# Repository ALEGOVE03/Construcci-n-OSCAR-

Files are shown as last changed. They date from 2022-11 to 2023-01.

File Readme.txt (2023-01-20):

Este repositorio contiene todo lo necesario para construir OSCAR según las especificaciones del LIANA, se incluyen los archivos necesarios de manufactura de las piezas. Las cuales se desarrollaron mediante impresión 3D con filamento PLAmax, además se incluyen los archivos del PCB el cual se mandó a hacer en China. Para finalizar se incluyen los archivos de programación desarrollada mediante ROS noetic usando Python.

 El proyecto consiste en una plataforma robótica para hacer experimentos, cuenta con dos manipuladores THOR que se adaptaron según las necesidades del laboratorio y al ser modular cuenta con una gran flexibilidad para mejoras o cambios. Como parte de la documentación que se incluye están los planos, plan de manufactura, instrucciones de ensamble con lista de materiales y los archivos de programación documentado.

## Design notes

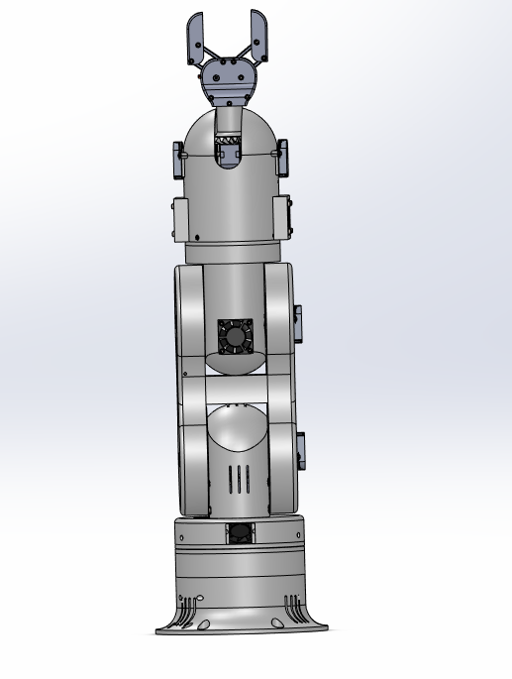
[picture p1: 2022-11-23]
OSCAR-THOR/STL/Sin título.png

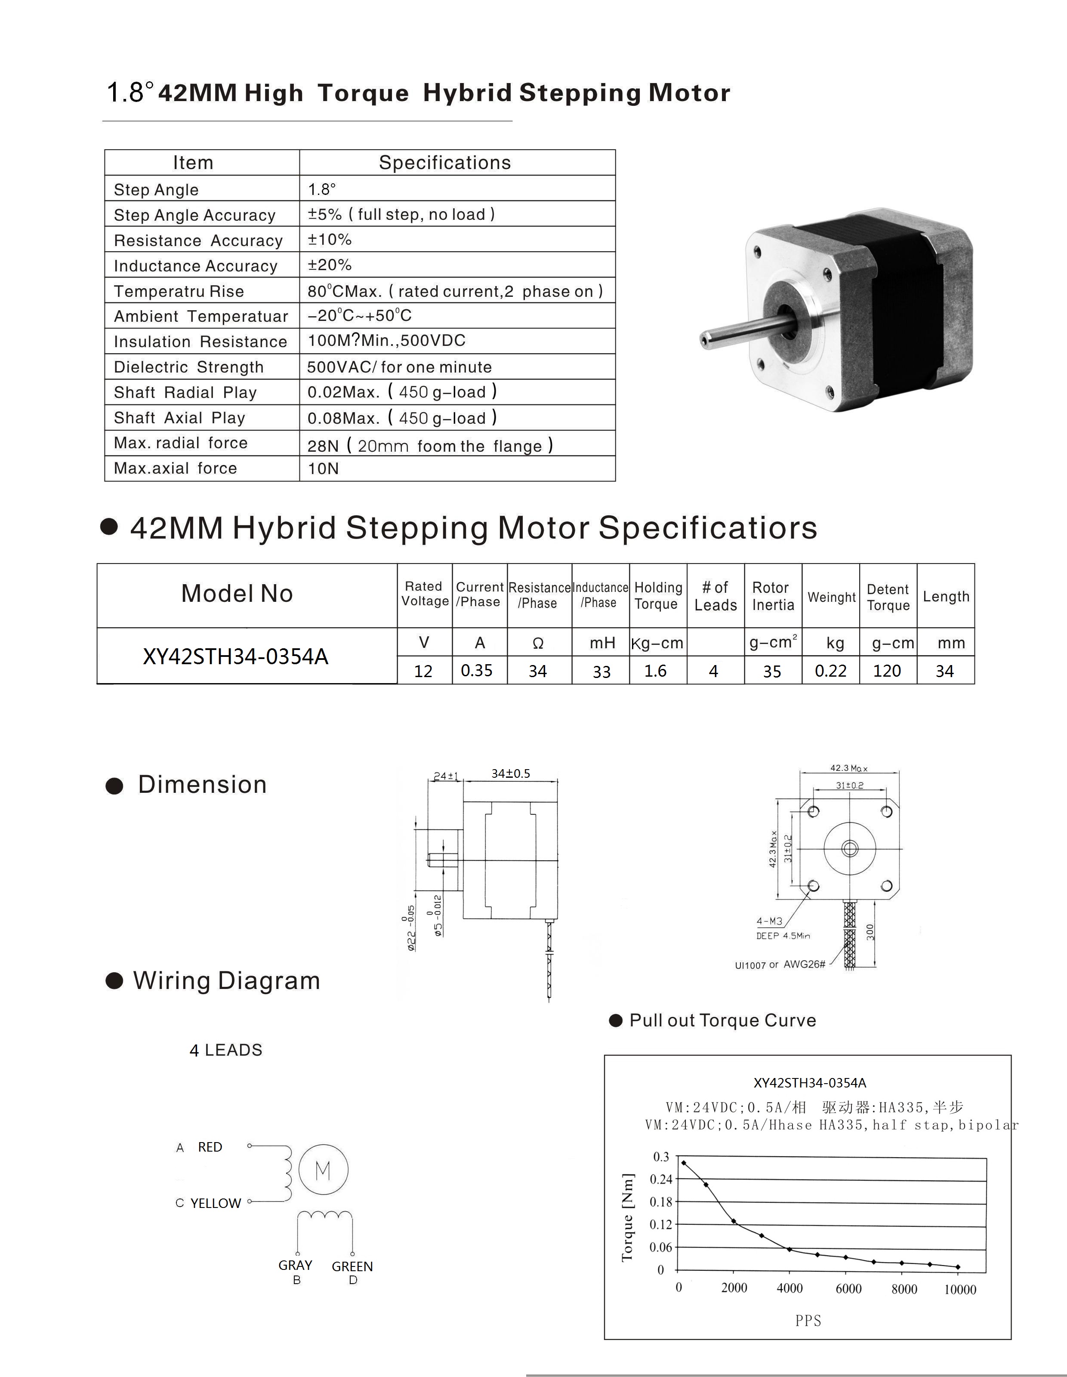
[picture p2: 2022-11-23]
Documentos/Hojas de datos/nema17_34_datasheet.jpg

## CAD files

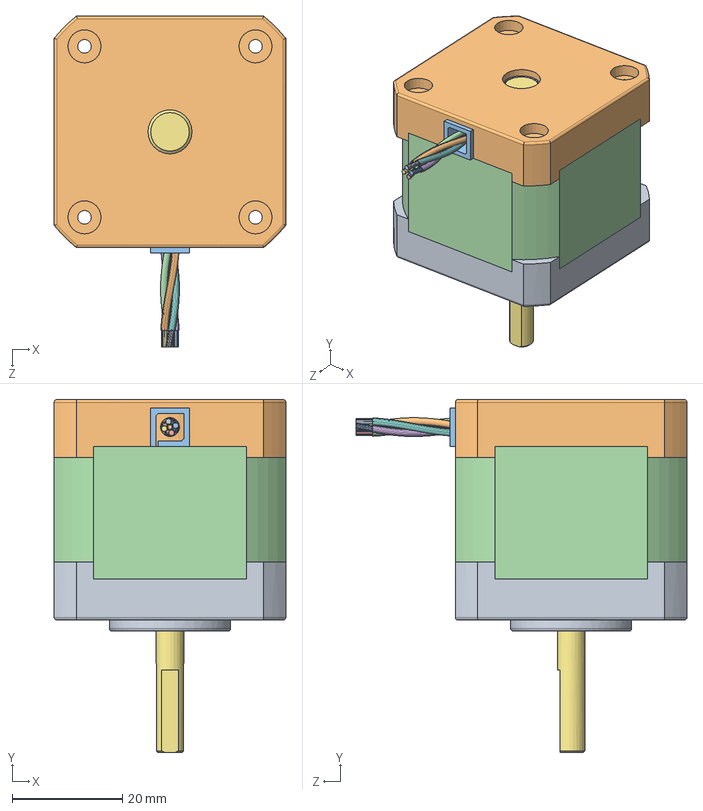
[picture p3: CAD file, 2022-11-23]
OSCAR-THOR/Componentes/NEMA17 x 40.SLDASM
42.0 x 64.0 x 60.0 mm
Frontplate.step
Backplate.step
Connenctor.step
Housing.step
Bearing dummy.step
Bearing dummy 01.step
Core.step
Cable-1of4.step
Copper-1of4.step
Cable-2of4.step
Copper-4of4.step
Cable-3of4.step
Copper-3of4.step
Cable-4of4.step
Copper-2of4.step

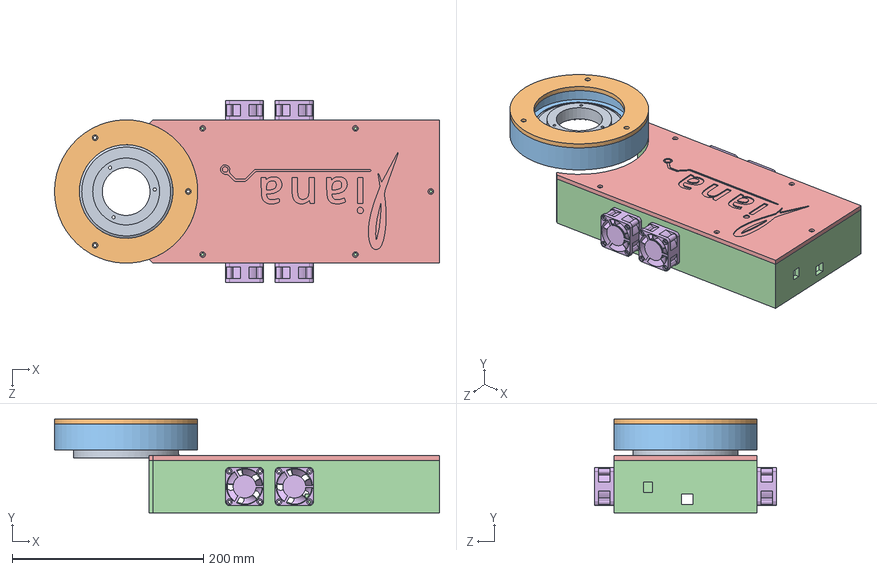
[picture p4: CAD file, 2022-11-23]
OSCAR-THOR/Ensamble URDF/Base_link/Base.SLDASM
402.9 x 98.0 x 190.0 mm
Art1Bot
BaseBearingFix
BaseTop
BaseCase
CaseTop}
40mm fan x 4

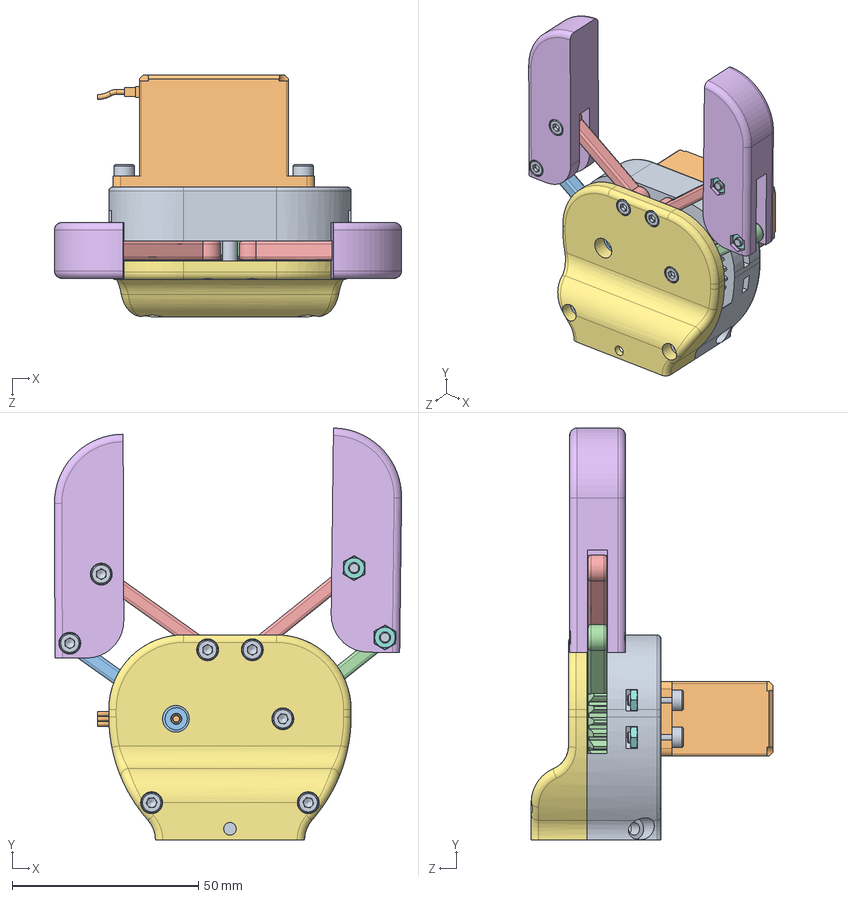
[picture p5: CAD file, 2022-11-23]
OSCAR-THOR/Ensamble URDF/Gripper/gripper.SLDASM
93.1 x 110.5 x 64.8 mm
GripperBot
MG996R
GripperActiveArm
GripperPassiveArm
GripperArm x 2
GripperFinger x 2
GripperTop
hexagon nut_3_jis x 13
socket head cap screw_am x 13

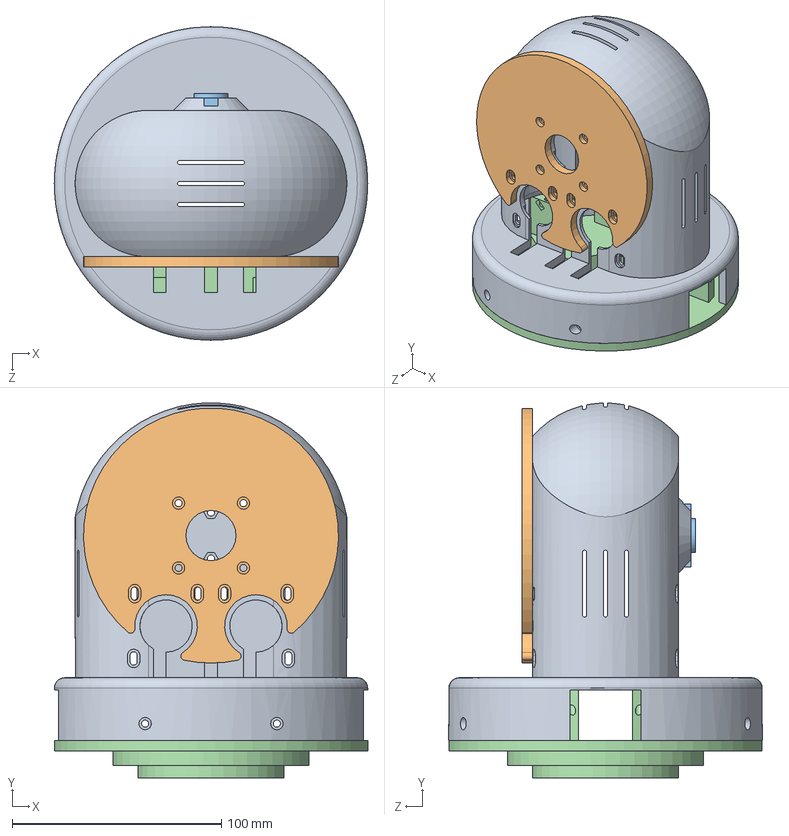
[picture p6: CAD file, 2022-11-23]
OSCAR-THOR/Ensamble URDF/Link_1/ART1.SLDASM
150.0 x 179.4 x 150.0 mm
Art1Body
Art2BodyACover1
AxisFix
Art1Top

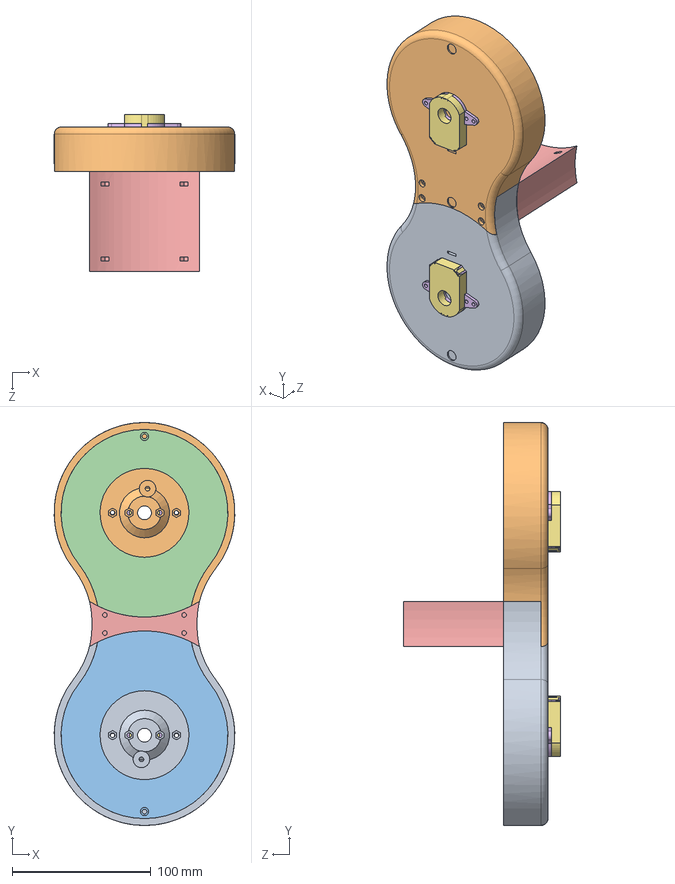
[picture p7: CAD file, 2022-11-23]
OSCAR-THOR/Ensamble URDF/Link_2/ART2_2.SLDASM
129.9 x 290.0 x 113.0 mm
Art2BodyB_Splitted_A
Art2BodyB_Splitted_B
Art2BodyBCover_Splitted_A
Art2BodyBCover_Splitted_B
Art2BodyUnion
AMT-B0-W x 2
AMT x 2

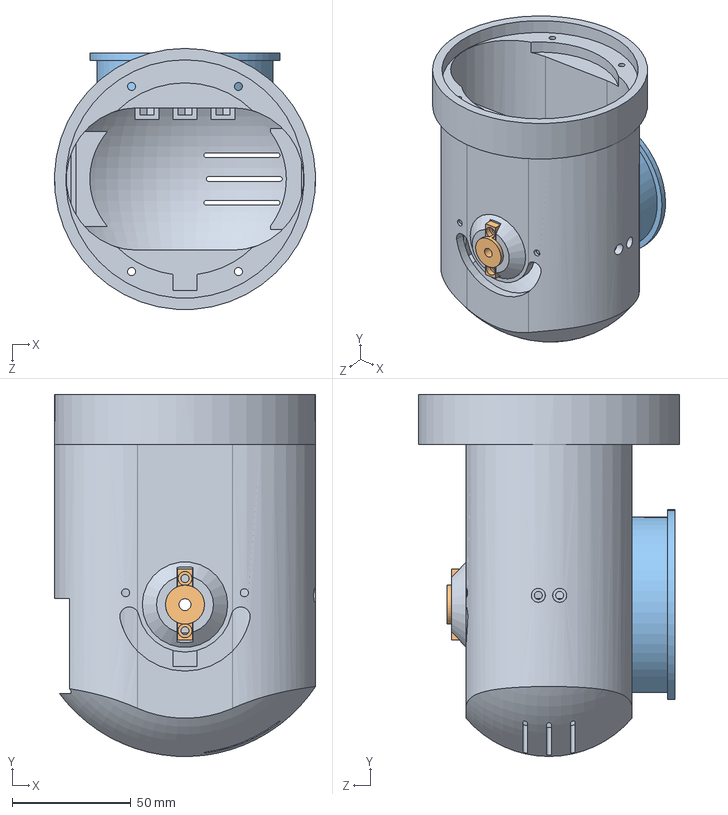
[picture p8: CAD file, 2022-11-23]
OSCAR-THOR/Ensamble URDF/Link_3/ART3&4.SLDASM
110.0 x 152.5 x 110.0 mm
Art3Body
AxisFix
Art3Pulley
CommonBearingFixThrough

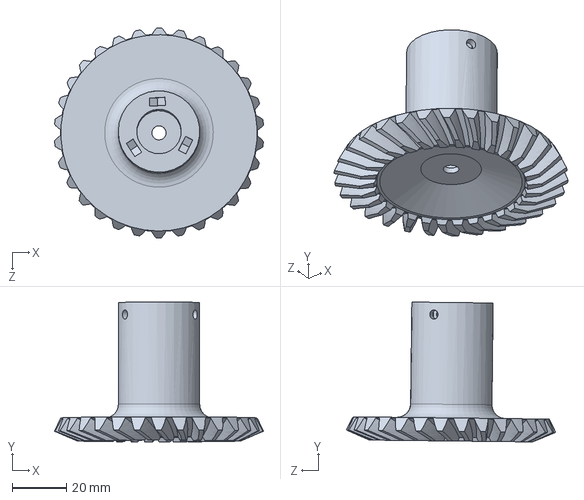
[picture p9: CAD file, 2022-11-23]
OSCAR-THOR/Ensamble URDF/Link_6/Link6.SLDASM
77.0 x 51.5 x 77.2 mm

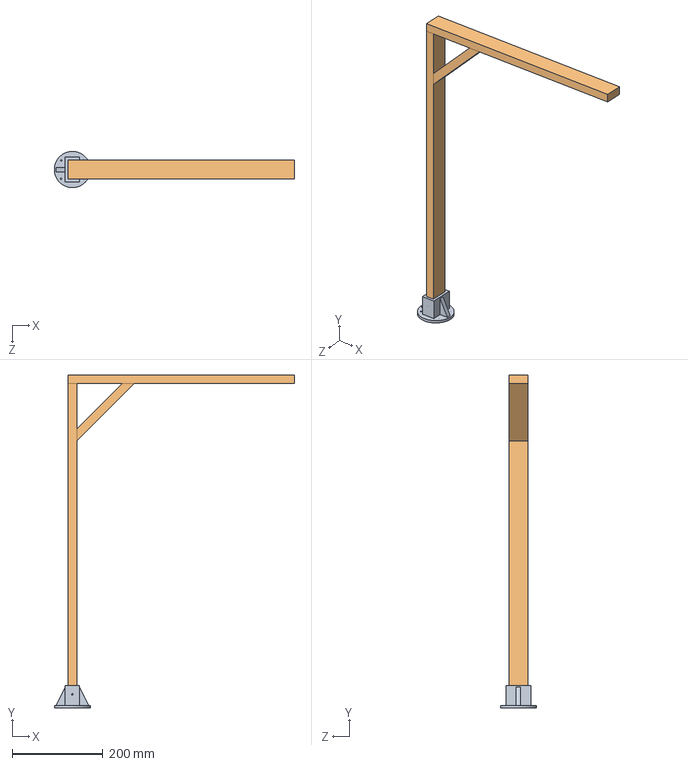
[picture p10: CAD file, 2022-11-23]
OSCAR-THOR/Ensamble URDF/Soportecamara/soporte.SLDASM
530.8 x 735.0 x 79.9 mm
UnionSoporte
soporte

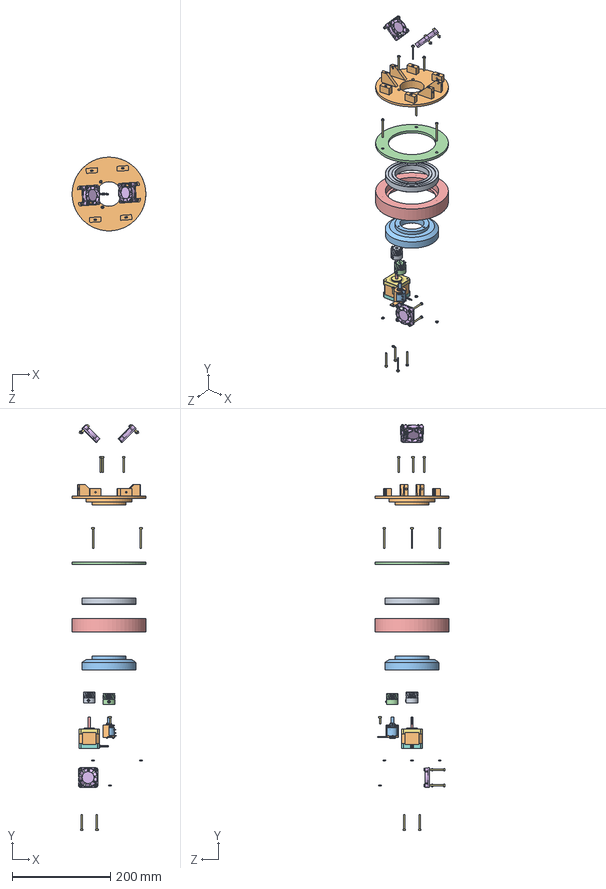
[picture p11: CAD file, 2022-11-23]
OSCAR-THOR/Ensambles/Base.SLDASM
150.0 x 825.8 x 149.9 mm
Art1GearMotor
Art1Top
Art1Bot
BaseBearingFix
BaseTop
fan 40mm x 3
Frontplate.step
Backplate.step
Connenctor.step
Housing.step
Bearing dummy.step
Bearing dummy 01.step
Core.step
Cable-1of4.step
Copper-1of4.step
Cable-2of4.step
Copper-4of4.step
Cable-3of4.step
Copper-3of4.step
Cable-4of4.step
Copper-2of4.step
hexagon nut_3_jis x 21
socket head cap screw_am2 x 19
socket button head cap screw_am x 2
radial ball bearing_68_am
Art1PotMount
Potentiometer
Art1GearPot

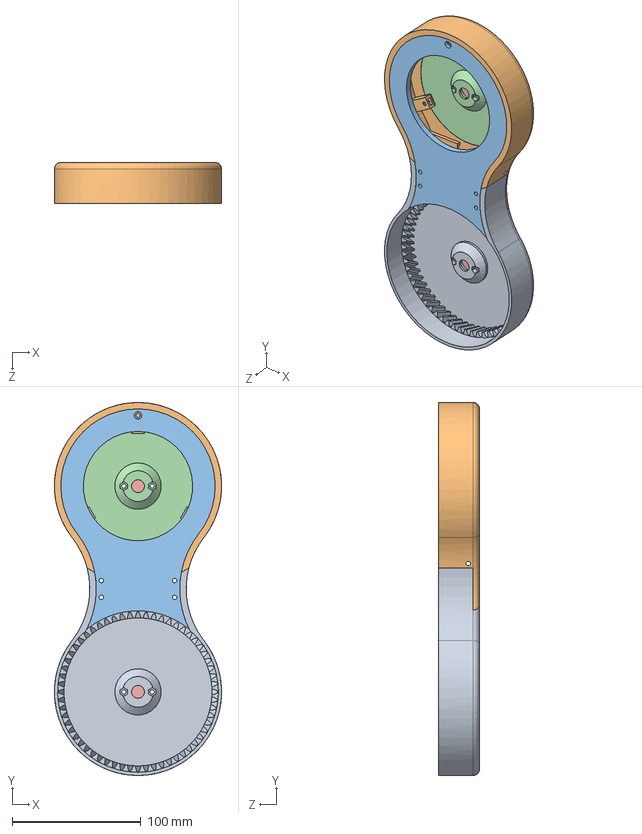
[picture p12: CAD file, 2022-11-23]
OSCAR-THOR/Ensamble URDF/Link_2/ART2_1.SLDASM
129.9 x 290.0 x 32.0 mm
Art2BodyA_Splitted_A
Art2BodyA_Splitted_B
Art2BodyACover2
Art2BodyAWindow
CommonBearingFix x 2

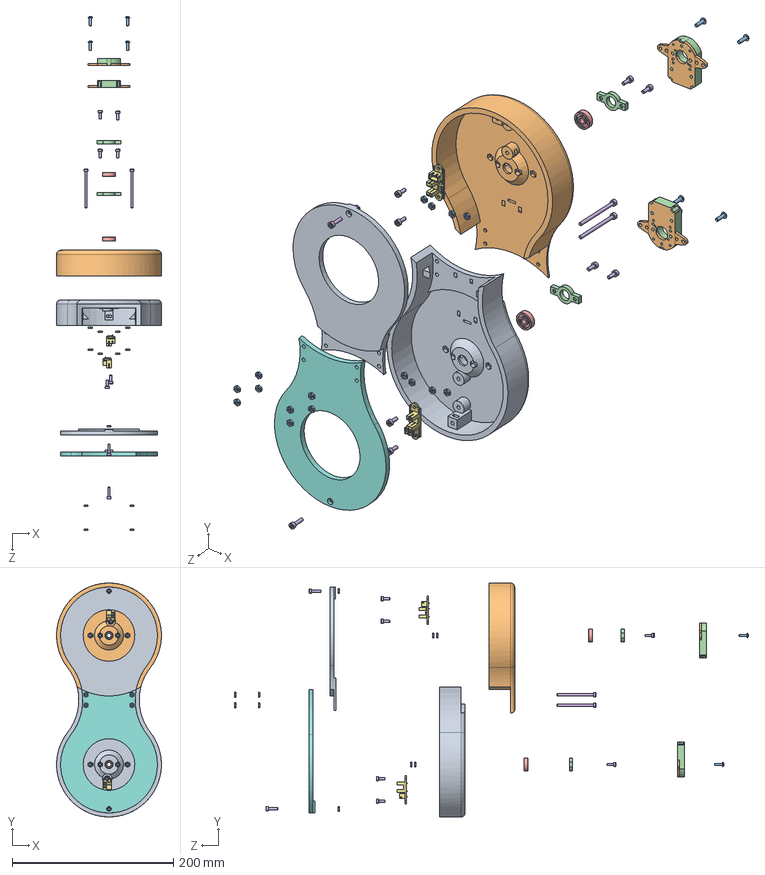
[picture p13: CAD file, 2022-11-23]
OSCAR-THOR/Ensambles/ART2_2.SLDASM
129.9 x 290.0 x 637.2 mm
Art2BodyB_Splitted_A
Art2BodyB_Splitted_B
hexagon nut_3_jis x 22
CommonBearingFixThrough x 2
radial ball bearing_68_skf x 2
socket head cap screw_am x 14
Lerdge Optical End Stop x 2
Art2BodyBCover_Splitted_A
Art2BodyBCover_Splitted_B
AMT-B0-W x 2
socket button head cap screw_am x 4
AMT x 2

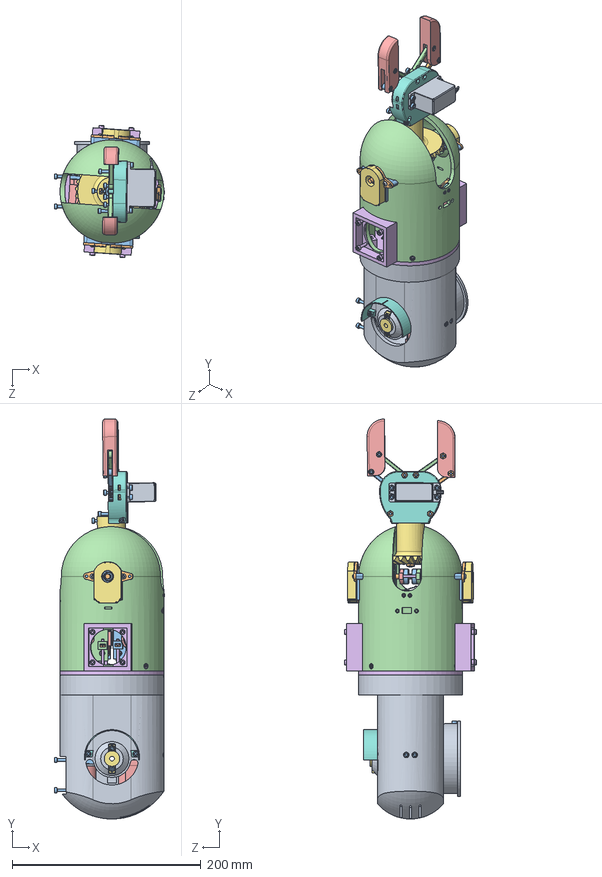
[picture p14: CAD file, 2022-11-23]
OSCAR-THOR/Ensambles/TOP UNION.SLDASM
116.7 x 423.8 x 140.2 mm
Art3Body
hexagon nut_3_jis x 69
socket head cap screw_am x 46
Art4MotorFix
Nema 17x34 x 3
Art4MotorGear
AxisFix
Art23Optodisk
Art3Pulley
CommonBearingFixThrough
radial ball bearing_68_skf x 6
Art4PotGear
Potentiometer Housing.stp
Potentiometer Pin.stp x 3
Potentiometer Threaded Tube.stp
Potentiometer Shaft.stp
ASME B27.8M 3FM1-7.stp
3,8 - 32UNEF Hex Nut.stp
Art4PotMount
Art4Body
CoverRingBolt
socket head cap screw_am3 x 41
Art56GearPlate
GT2_40teeth_5bore x 2
socket button head cap screw_am x 5
66x5mm eje art56 x 2
EncoderMount x 2
Bottom.step
Pin_NC.step
Pin_NO.step
Pin_C.step
Top.step
Button.step
Lever.step
Art56MotorHolderA x 2
Art56MotorHolderB x 2
GT2_20Teeth_5bore x 2
Art4BodyBot
Art4TransmissionColumn
Art4BearingRing
Art4BearingPlug
AMT-B0-W x 2
hexagon socket button head screw_jis
CoverRingNut
bola6mm
Art4BodyFan x 2
AMT x 2
GripperBot
MG996R
GripperActiveArm
GripperPassiveArm
GripperArm x 2
GripperFinger x 2

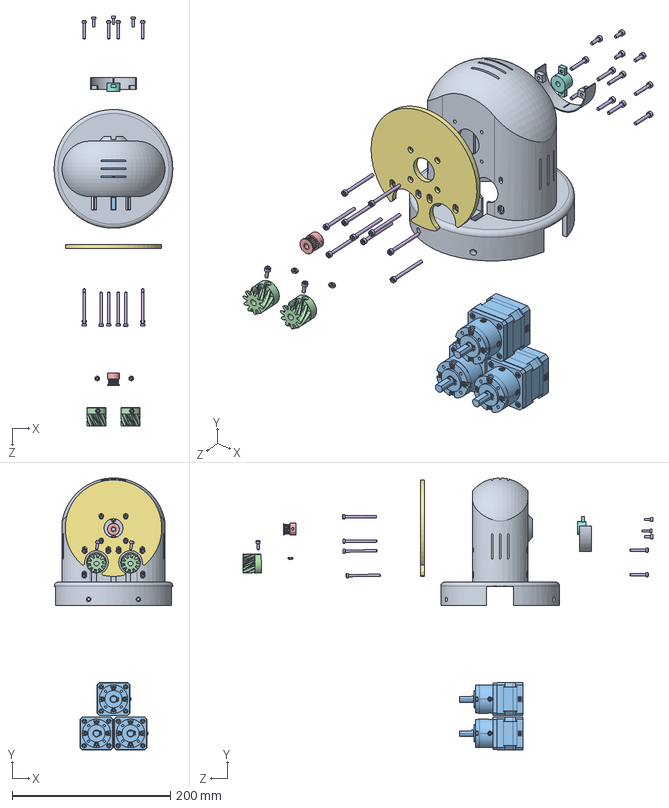
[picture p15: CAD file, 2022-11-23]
OSCAR-THOR/Ensambles/ART1.SLDASM
150.0 x 343.8 x 518.2 mm
Art1Body
hexagon nut_3_jis x 6
Nema17x34Gearbox x 3
Art2MotorGear x 2
GT2_20Teeth_5bore
socket head cap screw_am x 24
Art2BodyACover1
AxisFix
Art23Optodisk

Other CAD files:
OSCAR-THOR/Componentes/pot/ASME B27.8M 3FM1-7.stp.SLDPRT
OSCAR-THOR/Componentes/40mm fan.SLDPRT
OSCAR-THOR/Componentes/GT2_20Teeth_5bore.SLDPRT
OSCAR-THOR/Componentes/GT2_40.SLDPRT
OSCAR-THOR/Componentes/GT2_40teeth_5bore.SLDPRT
OSCAR-THOR/Componentes/Lerdge Optical End Stop.SLDPRT
OSCAR-THOR/Componentes/MF84ZZ.SLDPRT
OSCAR-THOR/Componentes/MG996R.SLDPRT
OSCAR-THOR/Componentes/Microswitch.SLDPRT.SLDASM
OSCAR-THOR/Componentes/Nema 17x34.SLDPRT
OSCAR-THOR/Componentes/Nema17x34Gearbox.SLDPRT
OSCAR-THOR/Componentes/ejes/14.5x5mm eje art1.SLDPRT
OSCAR-THOR/Componentes/ejes/142x5mm eje art3.SLDPRT
OSCAR-THOR/Componentes/ejes/14x4mm eje faja.SLDPRT
OSCAR-THOR/Componentes/ejes/46x5mm eje art2.SLDPRT
OSCAR-THOR/Componentes/ejes/66x5mm eje art56.SLDPRT
OSCAR-THOR/Componentes/encoder/AMT-B0-W.SLDPRT
OSCAR-THOR/Componentes/encoder/AMT.SLDPRT
OSCAR-THOR/Componentes/endstop/Bottom.step.SLDPRT
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

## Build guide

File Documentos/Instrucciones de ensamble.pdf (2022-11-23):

# INSTRUCCIONES DE ENSAMBLE

I I S e m e s t r e 2 0 2 2

## Tabla de contenido

Descripción | 1
Gripper | 3
Articulación 5 & 6 | 7
Articulación 3& 4 | 15
Unión Superior | 21
Articulación 1 | 22
Articulación 2 ladoA | 26
Articulación 2 ladoB | 30
Unión media | 33
Base | 35
Unión inferior | 42
Unión Base-Case | 43
Conexión electrica | 46

1

# DESCRIPCIÓN

Este documento se encuentra la información necesaria para montar y desmontar el brazo THOR utilizado como un componente de OSCAR, proyecto desarrollado en el Laboratorio de inteligencia Artificial para las ciencias naturales LIANA del área académica de mecatrónica en el instituto tecnológico de Costa Rica. El montaje y desmontaje del brazo es un proceso bastante largo y se debe de tener cuidado especialmente con cables y piezas frágiles, además el orden es imprescindible para pasar los cables a través de las piezas. Cada articulación se explica como un pequeño ensamble, así se pueden armar las partes con más detalle. En este documento también se incluye todo el armado eléctrico, eso quiere decir que se incluye la codificación de colores de los cables, el nombre de cada cable a cada componente y la conexión al PCB.

Este instructivo se desarrolló con el propósito de ser usado en laboratorio para ayudar a entender como esta armado el brazo en caso de dar algún mantenimiento o la construcción de otro brazo, además este documento se puede modificar según las necesidades del LAIANA.

Herramientas necesarias para el armado:

- Alicate de puntas
- Llave Allen para tornillos M3 y M5
- Adhesivo liquido

Herramientas necesarias para el PCB y la conexión de cables:

- Cautín y soldadura
- Cuchilla o cortadora para pelar cable

2

Lista de materiales para cada brazo THOR

Componente Cantidad
Gripper
Tuerca M3 | 13
M3x12 | 9
M3x20 | 4
Articulación 56
Tuerca M3 | 37
Tuerca M5seguridad | 1
M3x25 | 8
M3x20 | 10
M3x10 | 4
M3x16 | 4
M3x10 cabeza plana | 6
M3x12 | 4
M3x35 | 4
Articulación 34
Tuerca M3 | 18
M3x10 | 14
M3x16 | 3
M3x20 | 2
M3x25 | 3
Articulación 1
Tuerca M3 | 6
M3x10 | 6
M3x20 | 8
M3x40 | 10
Articulación 2 lado A
Tuerca M3 | 10
M3x10 | 4
M3x12 | 4
M3x25 | 2
Articulación 2 lado B
Tuerca M3 | 22
M3x10 | 8
M3x10 cabeza plana | 4
M3x12 | 2
M3x45 | 4
Componente | Cantidad
Base
Tuerca M3 | 21
M3x10 | 2
M3x12 | 1
M3x16 | 2
M3x20 | 4
M3x30 | 3
M3x40 | 9
Case
Tuerca M3 | 26
M3x10 | 10
M3x20 | 16
Tuerca M5 | 4
M5x25 | 4
Unión superior
M3x12 | 3
M3x20 | 4
Unión media
Mx45 | 4
Unión inferior
M3x16 | 4
Componente | Cantidad
PCB
JST 2 pines | 11
JST 3 pines | 4
JST 4 pines | 12
Capacitor 100uF/35V | 7
Capacitor 10uF/100V | 1
Capacitor 0.1uF/50V | 1
Regulador LM7805 | 1
Resistencia 10K | 1
8xPines hembra | 14
40Pines machos | 5
Conector DC barrel | 1
Driver A4988 | 7
Arduino Mega | 1

3

# GRIPPER

Paso 1
Colocar una tuerca M3 en el orificio mostrado de la pieza GripperBot. Se puede poner una gotita de algún adhesivo para dejar la tuerca en su lugar de ser necesario.

Paso 2
Colocar 4 tuercas M3 en los orificios laterales de la pieza GripperBot.

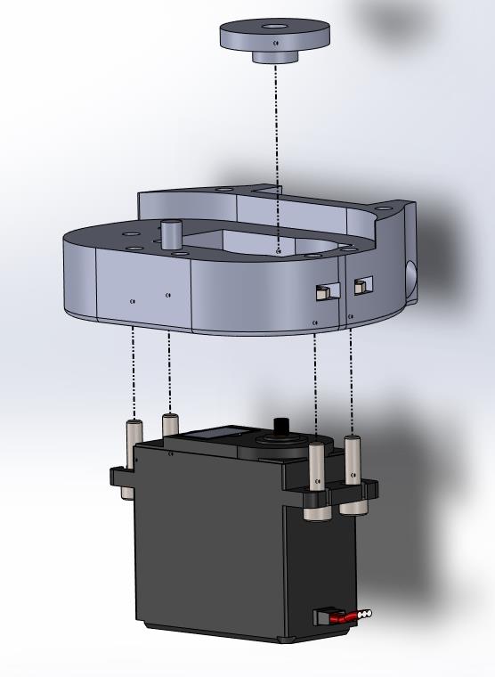
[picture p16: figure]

4

Paso 3
Con 4 tornillos M3x12 se debe asegurar el servo MG996 a la pieza GripperBot, luego se debe colocar el acople que incluye el servo

Paso 4
Se colocan 4 tuercas M3 en los orificios indicados de la pieza GripperBot. En caso de ser necesario las tuercas se pueden asegurar en su lugar con algún adhesivo.

5

Paso 5
Se deben colocar las piezas tal que los GripperArm van en los agujeros del frente, el GripperPassiveArm va atrás junto con el GripperActiveArm que se sujeta al acople del motor mediante dos tornillos en los agujeros de los extremos de la piza.

Paso 6
Se colocan los tornillos M3x20 en los orificios de la pieza GripperTop para sujetar los GripperArm y el GripperPassiveArm, para el caso del GripperActiveArm se termina de sujetar con el acople al servo mediante los tornillos que se incluyen con el servo.

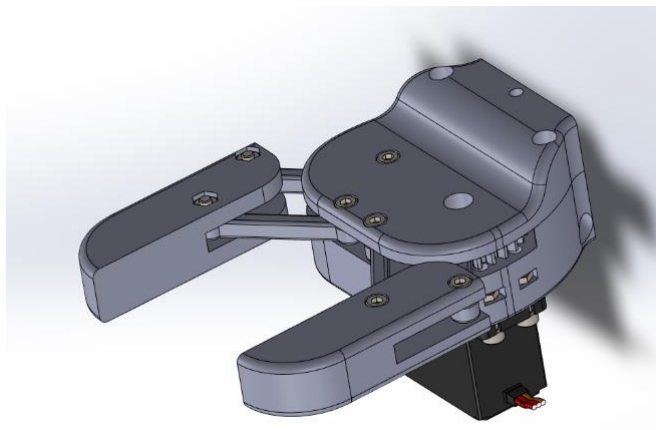
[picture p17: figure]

6

Paso 7
Mediante tornillos M3x12 con sus respectivas tuercas se unen los GripperFinger a los GripperArm tal como se muestra.

Paso 8
El gripper final se debería ver de la siguiente forma, se debe tener cuidado con no presionar los tornillos de la pinza a punto de que estos no se puedan rotar para abrir y cerrar la pinza.

7

# ARTICULACIÓN 5 & 6

Paso 1
Colocar la tuerca de seguridad M5 en la pieza Art56MotorCoverRing tal como se muestra, la tuerca se introduce por los costados y se coloca en la ranura, se debe colocar algún adhesivo para mantener la tuerca en su lugar y sea más fácil su manipulación.

Paso 2
A la pieza Art56MotorCoverRing se le introducen los rodamientos 625 seguido de las piezas CoverRingBolt y CoverRingNut para mantenerlos en su lugar, luego a estas se le colocan dos tornillos M3x20 con sus respectivas turcas M3.

8

Paso 3
Se introduce el rodamiento 625 en la pieza Art56GearPlate, seguido va el tornillo M5x16 que asegura el conjunto a la pieza Art56MotorCoverRing permitiendo rotar la estructura. Por ultimo se colocan 3 tuercas M3 en las ranuras superiores del Art56GearPlate.

Paso 4
Colocar dos tuercas M3 en las ranuras interiores de la pieza Art4Body, seguido de un rodamiento 625 en el orificio externo, a la pieza EncoderMount se le colocan 2 tuercas M3 y se asegura a la pieza Art4Body mediante 2 tornillos M3x10.

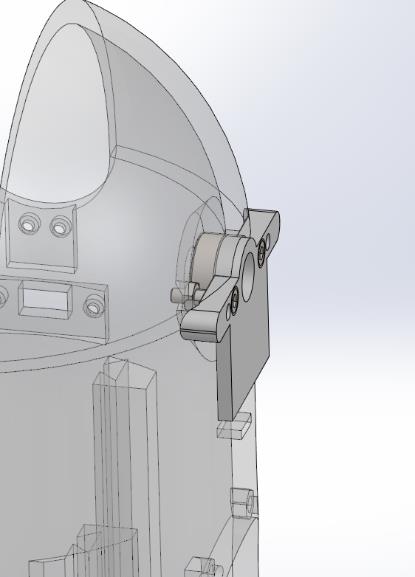
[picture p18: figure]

9

Paso 5
El paso 4 se debe repetir para el lado opuesto ya que estos rodamientos sirven como soporte de los ejes de las poleas.

Paso 6
Las piezas Art56SmallGear se colocan a las poleas de GT2 de 20 dientes, luego se colocan los tornillos M3x10 de cabeza plana pero no se introducen por completo, primero se deben de poner en posición.

10

Paso 7
Se introducen las partes previamente ensambladas como se muestra, los ejes de 66x5mm se colocan de forma que la polea este soportada en el eje entre los rodamientos de las piezas Art4Body y Art56MotorCoverRing. No se debe olvidar introducir las fajas de 200mm que están en las poleas.

Paso 8
A los motores a pasos Nema17-34 se les debe colocar la pieza Art56MotorHolderA al frente y se sujeta mediante tornillos M3x8 y la pieza Art56MotorHolderB por detrás mediante tornillos M3x25. Los triángulos salidos deben estar del mismo lado ya que estos se insertan en la pieza Art4Body. Finalmente se colocan las poleas de los motores. Se colocan tuercas M3 en las ranuras salidas que tiene las piezas, ya que luego sirve para tensar la faja.

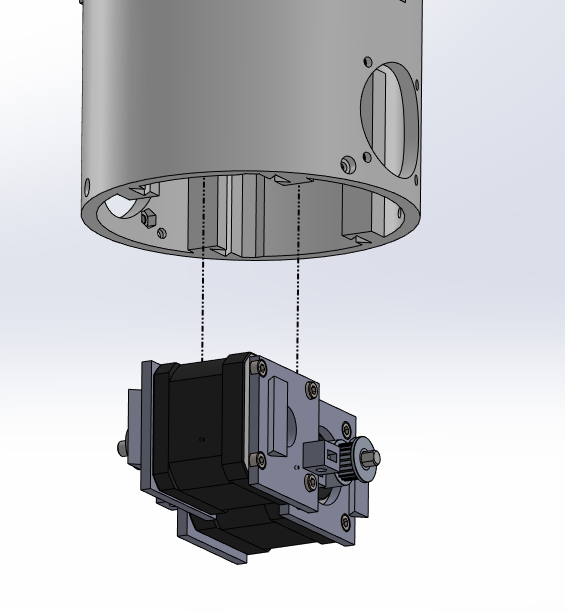
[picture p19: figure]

11

Paso 9
Se introducen los motores en los rieles tal como se muestra, se debe tener cuidado con las tuercas, de ser necesario se puede usar un poco de adhesivo para mantenerla en su lugar. La faja se debe montar en la polea del motor para conectar el Art56SmallGear con el motor a pasos.

Paso 10
Se colocan tuercas M3 en el interior de la pieza Art4Body como se muestra, se pasa el cable del ventilador por dentro de la pieza Art4BodyFan como se muestra. Aun no se debe asegurar las piezas con tornillos M3x20 antes se debe verificar el motor a pasos tenga la faja bien colocada y que la pieza Art4BodyBot este en su lugar, vea el siguiente paso.

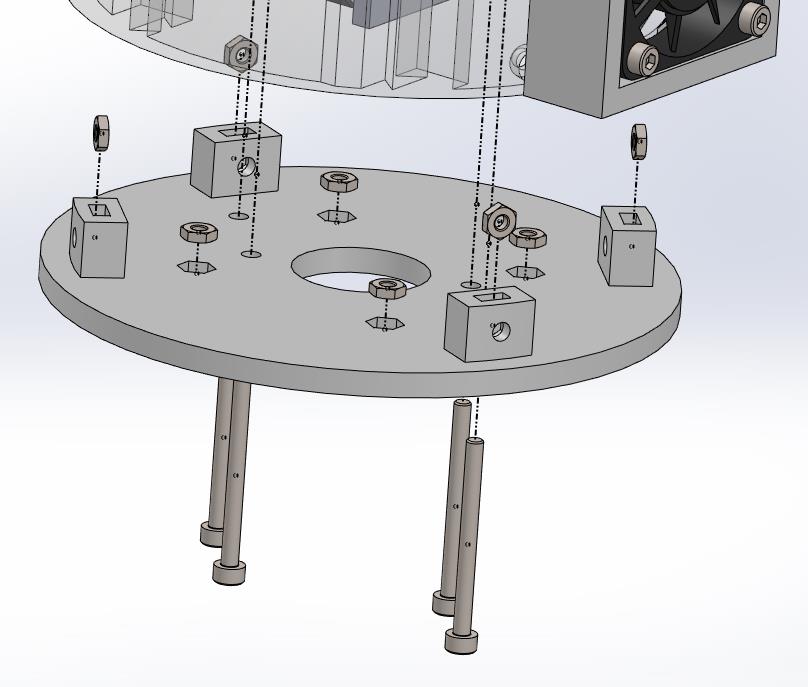
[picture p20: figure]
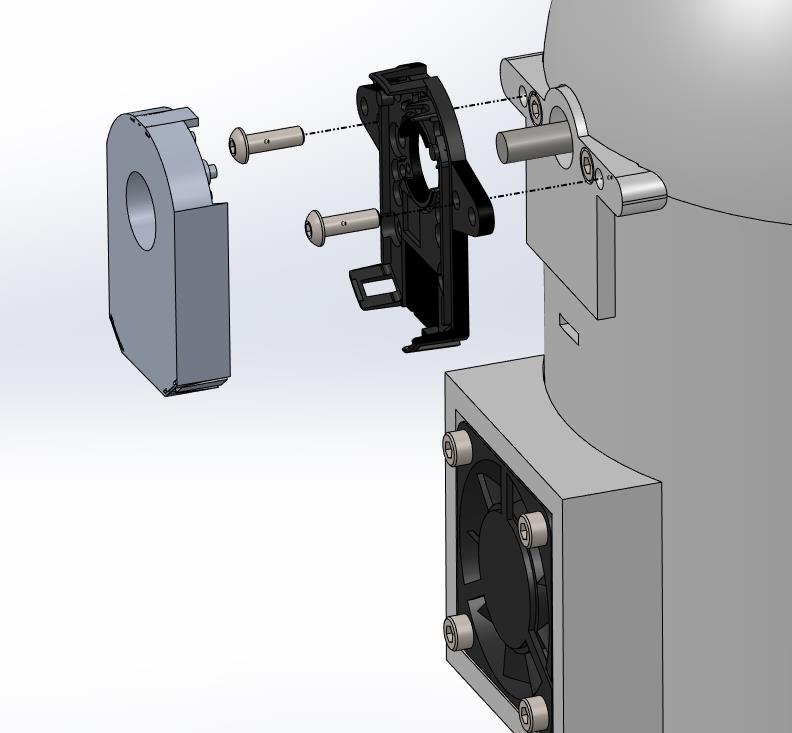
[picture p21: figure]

12

Paso 11
Se colocan las 8 tuercas M3 en la pieza Art4BodyBot, primero se usan los tornillos M3x12 para asegurarla a la pieza Art4Body en los 4 laterales, luego se usan los tornillos M3x35 para asegurar y tensar los motores. Finalmente se termina se asegurar los ventiladores del paso 10. No olvidar pasar todos lo cables de los motores y sensores.

Paso 12
Se instala el encoder siguiendo las instrucciones que se incluyen, recordar haber pasado el cable antes. Primero se coloca el adaptador al eje, luego la base y de ultimo el encoder.

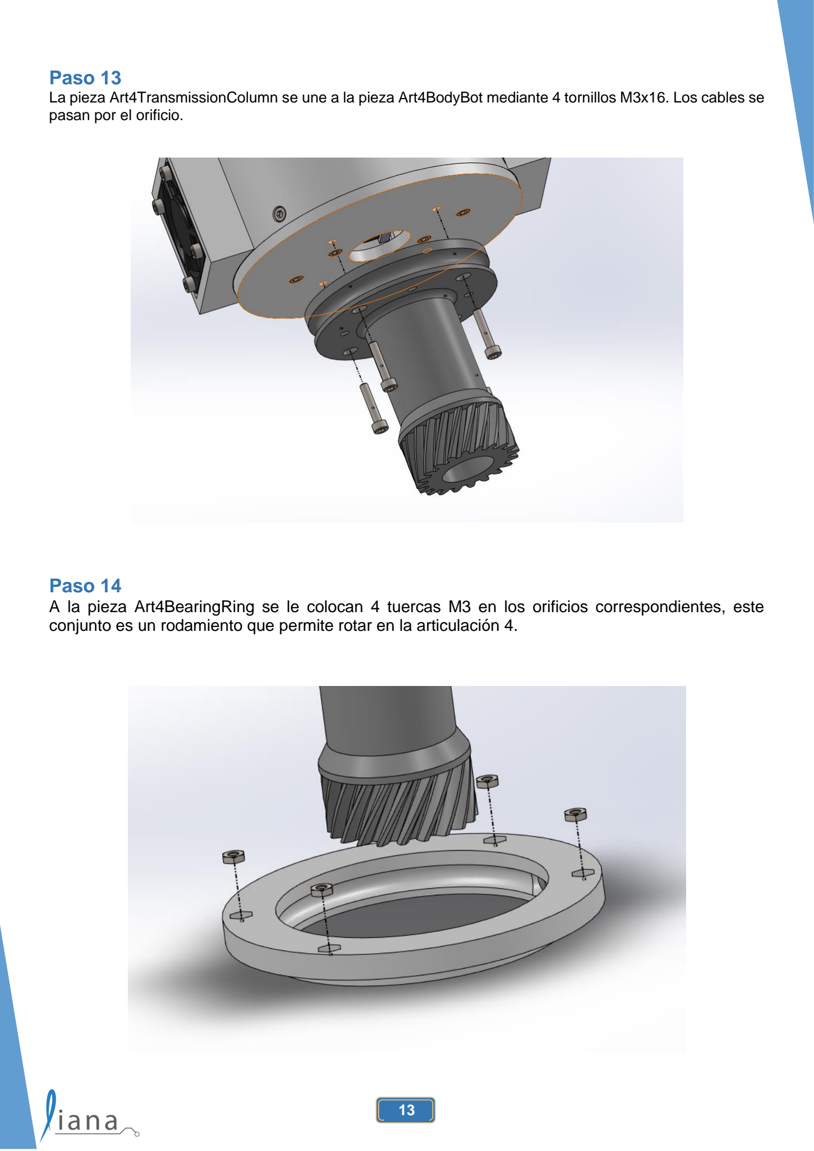
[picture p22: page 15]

13

Paso 13
La pieza Art4TransmissionColumn se une a la pieza Art4BodyBot mediante 4 tornillos M3x16. Los cables se pasan por el orificio.

Paso 14
A la pieza Art4BearingRing se le colocan 4 tuercas M3 en los orificios correspondientes, este conjunto es un rodamiento que permite rotar en la articulación 4.

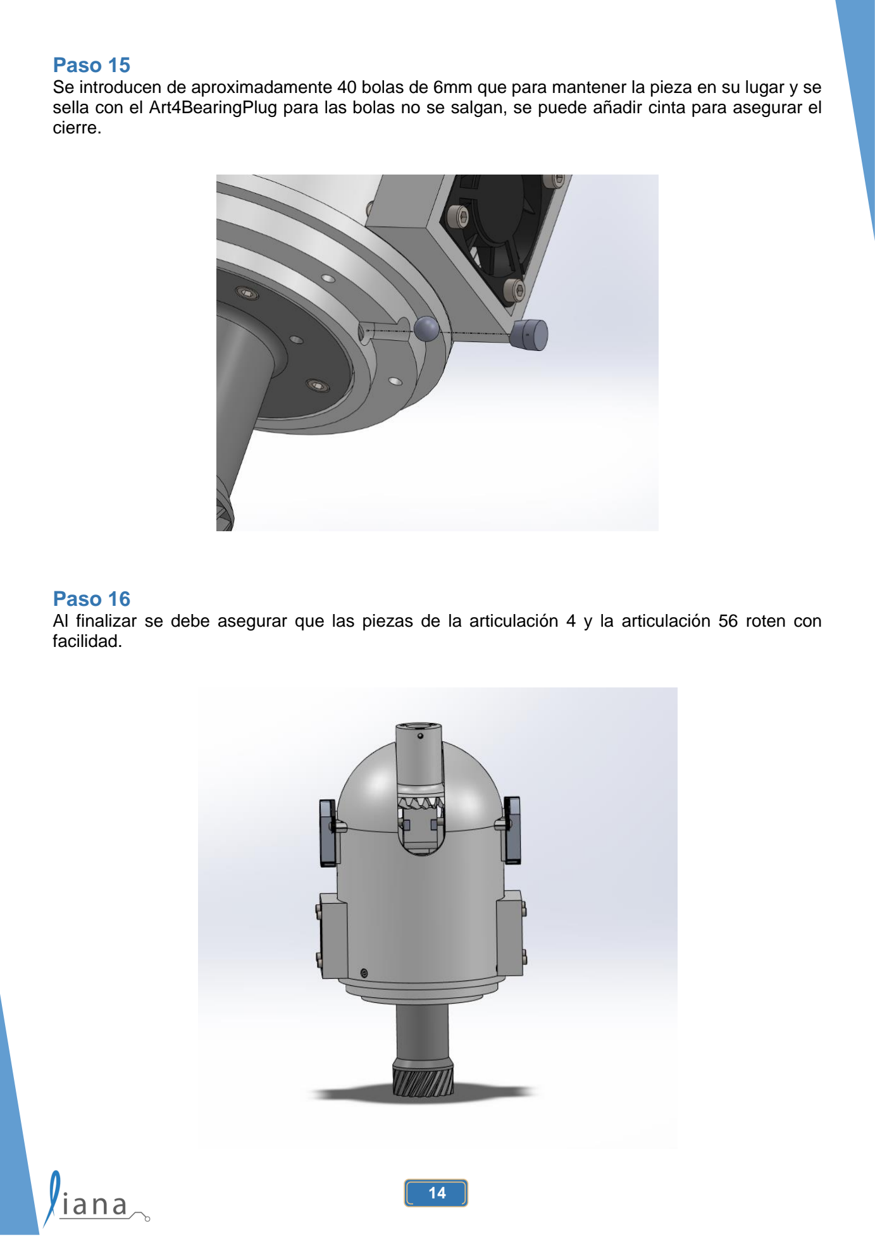
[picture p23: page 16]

14

Paso 15
Se introducen de aproximadamente 40 bolas de 6mm que para mantener la pieza en su lugar y se sella con el Art4BearingPlug para las bolas no se salgan, se puede añadir cinta para asegurar el cierre.

Paso 16
Al finalizar se debe asegurar que las piezas de la articulación 4 y la articulación 56 roten con facilidad.

15

# ARTICULACIÓN 3& 4

Paso 1
Primero se deben colocar la pieza Art4MotorFix al motor a pasos nema17-34 mediante 4 tornillos M3x8 y la pieza Art4PotMount se debe colocar al potenciómetro y se asegura mediante la tuerca que este incluye. A la pieza Art4MotorFix se deben agregar 2 tuercas M3 en las ranuras superiores.

Paso 3
Se deben agregar una tuerca M3 y un tornillo M3x 10 a las piezas Art4MotorGear y Art4PotGear.

16

Paso 4
Las piezas Art4MotorGear y Art4PotGear se colocan al motor y al potenciómetro respectivamente, tener cuidado que los diámetros de los ejes de estos.

Paso 5
Colocar 7 tuercas M3 en las ranuras interiores de la pieza Art3Body, de ser necesario se pude añadir adhesivo para mantener la tuerca en su lugar correcto.

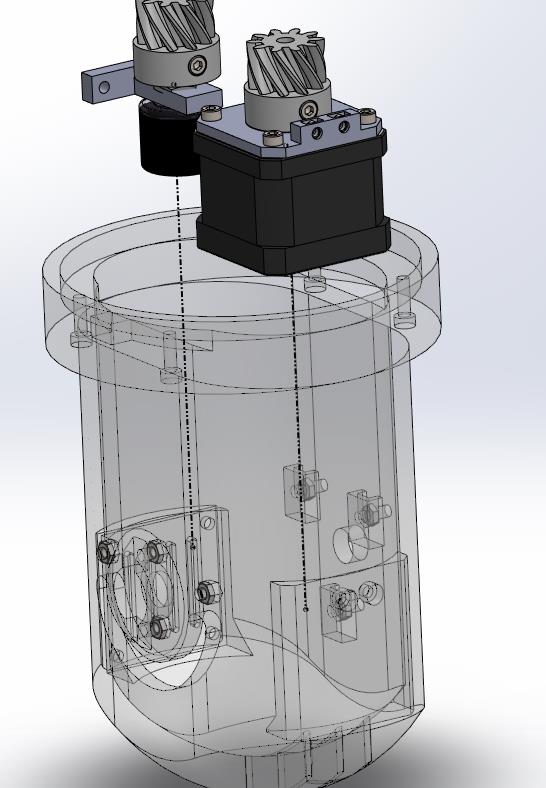
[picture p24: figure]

17

Paso 6
Colocar los conjuntos previos del motor y el potenciómetro dentro de la pieza Art3Body como se muestra, se debe tener cuidado con el lado de los cables y conectores.

Paso 7
El ventilador de 40x10mm se coloca en el exterior, teniendo cuidado con el flujo de aire. En la parte superior se colocar 2 tornillos M3x20 que también se encargan de asegurar el potenciómetro y 2 tornillos M3x16 en la parte inferior que solo sujeta el ventilador, se agregan sus tuercas M3 respectivas.

18

Paso 8
El motor se sujeta a la pieza Art3Body mediante 2 tornillos M3x10, el motor se monta en el escalón que tiene la pieza en su interior.

Paso 9
Para la polea en la parte superior se introduce un tonillo M3x16 con tuerca que sirve para sujetar la correa, en los laterales se deben introducir 2 tuercas M3 y en el lateral con la ranura más grande se inserta un rodamiento 625 seguido de la pieza CommonBearingFixThrough y se asegura con dos tornillos M3x10.

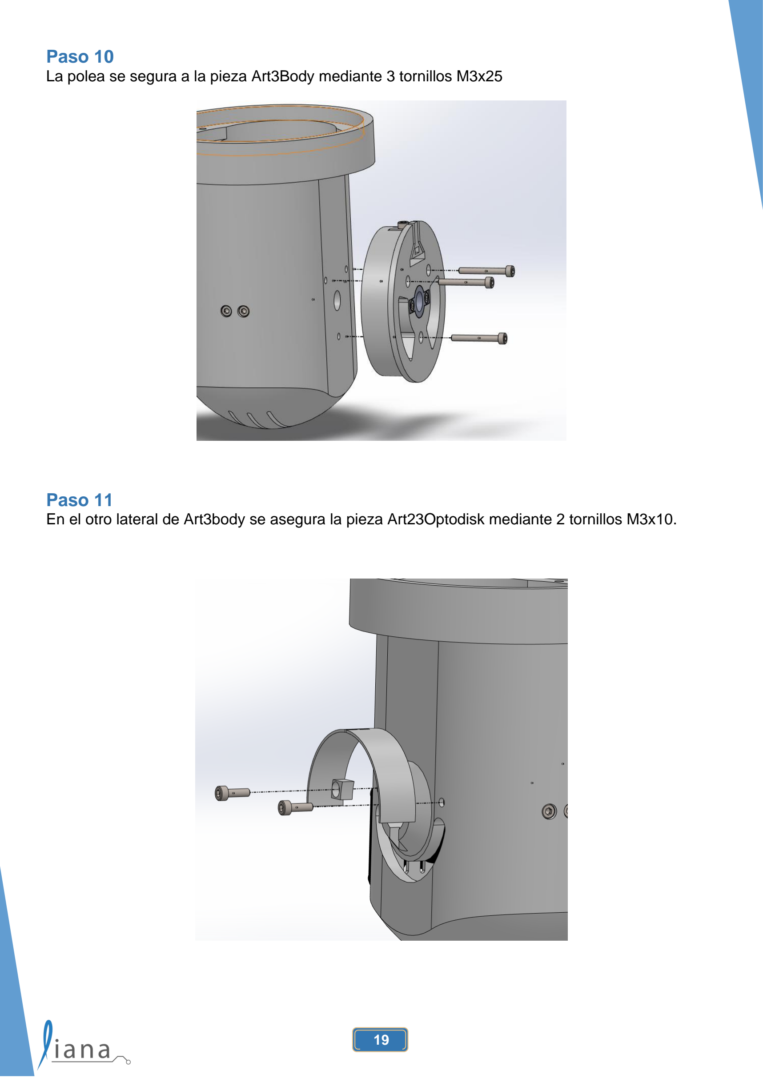
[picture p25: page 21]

19

Paso 10
La polea se segura a la pieza Art3Body mediante 3 tornillos M3x25

Paso 11
En el otro lateral de Art3body se asegura la pieza Art23Optodisk mediante 2 tornillos M3x10.

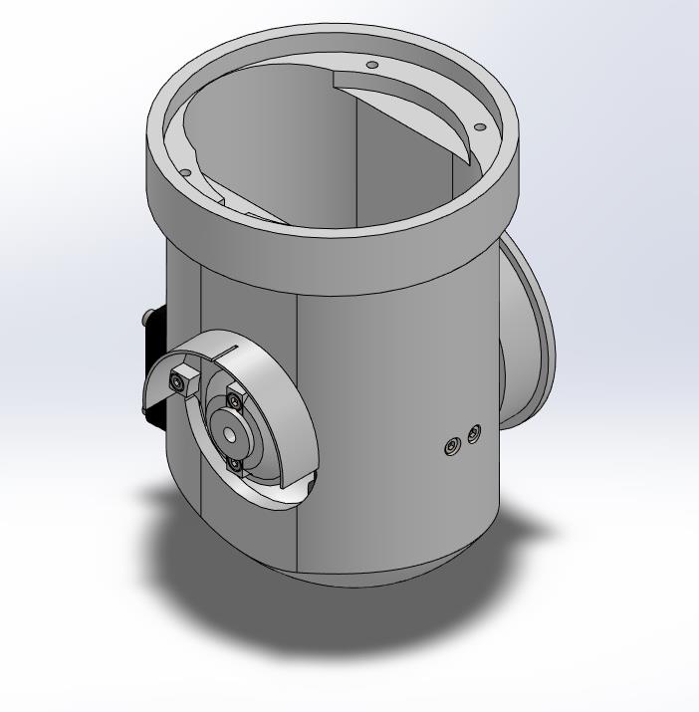
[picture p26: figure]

20

Paso 12
Se coloca la pieza AxisFix mediante 2 tornillos M3x10, se recomienda primero colocar y medir el eje para asegurarlo a esta pieza mediante un adhesivo fuerte, ya que el eje debe de rotar con toda la Art3Body.

Paso 13
Al finalizar se debe asegurar que las piezas de la articulación 34 estén bien aseguradas y que los cables estén bien conectados y no se enreden entre ellos o con alguna pieza que se mueva.

21

# UNIÓN SUPERIOR

Paso 1
El gripper o la pinza se asegura mediante 3 tornillos M3x12, recordar que se pueden colocar otro tipo de efectores que se adecuen a la forma de conectar con los tornillos.

Paso 2
La articulación 56 se asegura con la articulación 34 mediante 4 tornillos M3x20, se debe tener cuidado de que los engranes están bien puestos.

22

# ARTICULACIÓN 1

Paso 1
Se deben colocar 4 tuercas M3 en las ranuras interiores de la pieza Art1Body.

Paso 2
Se deben introducir los 3 motores nema17 con reducción 5:1 dentro de la pieza Art1Body, esta en la parte trasera se aseguran mediante 8 tornillos M3x20 y en la parte del frente se coloca primero Art2BodyACover1 seguido de los 10 tornillos M3x40.

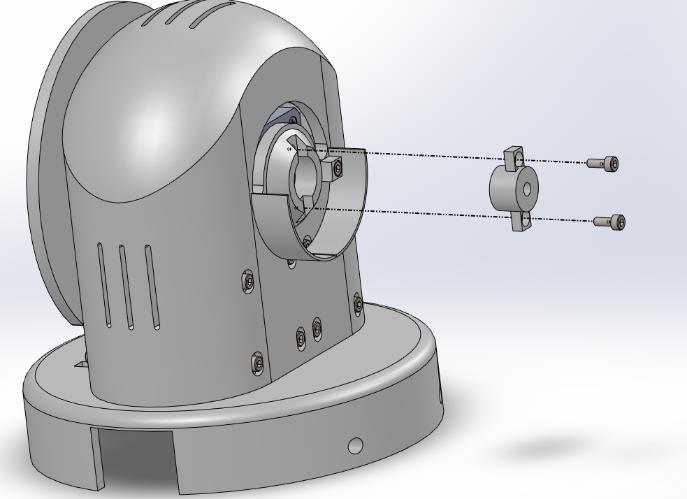
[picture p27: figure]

23

Paso 3
En el otro lateral de Art1body se asegura la pieza Art23Optodisk mediante 2 tornillos M3x10.

Paso 4
Se coloca la pieza AxisFix mediante 2 tornillos M3x10, se recomienda primero colocar y medir el eje para asegurarlo a esta pieza mediante un adhesivo fuerte, ya que el eje debe de esta fijo con la pieza Art1Body.

24

Paso 5
A las piezas Art2MotorGear se les debe agregar un tornillo M3x8 con su respectiva tuerca.

Paso 6
A los motores nema 17 se les colocan las piezas Art2MotorGear en los dos de abajo y en el motor de arriba se coloca la polea G2T.

25

Paso 7
Al finalizar asegurarse de que la articulación 1 tiene todas sus piezas bien aseguradas, tener cuidado con los cables de los motores y asegurar el espacio para pasar el resto de los cables.

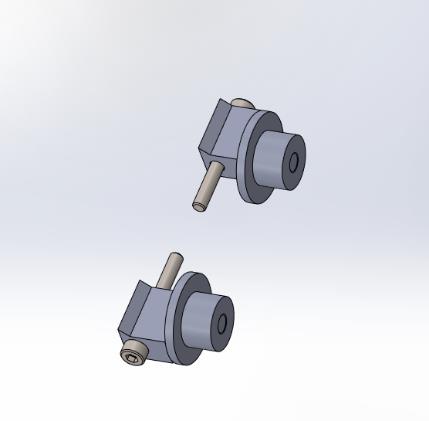
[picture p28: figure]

26

# ARTICULACIÓN 2 LADOA

Paso 1
Para formar las tensoras se le debe colocar una tuerca M3 y un tornillo M3x25 a la pieza Art3TensionerBody como se muestra, luego se le coloca el eje 14x4mm, el rodamiento MF84ZZ se coloca en la pieza Art3TensionerPulley y esta se monta sobre la otra parte del eje.

Paso 2
Las tensoras se deben ver como se muestran a continuación, una vez estén bien se colocan dentro de la pieza Art2BodyA_Splitted_B.

27

Paso 3
En la pieza Art2BodyA_Splitted_B se deben colocar 3 tuercas M3 como se muestra, en caso de ser necesario se le puede añadir un poco de adhesivo para mantenerlas en su lugar.

Paso 4
En la pieza Art2BodyAWindow se colocan 2 tuercas M3 en la parte posterior, en la delantera se coloca el rodamiento 625 y mediante la tapa CommonBearingFix se mantiene en su lugar con dos tornillos M3x10.

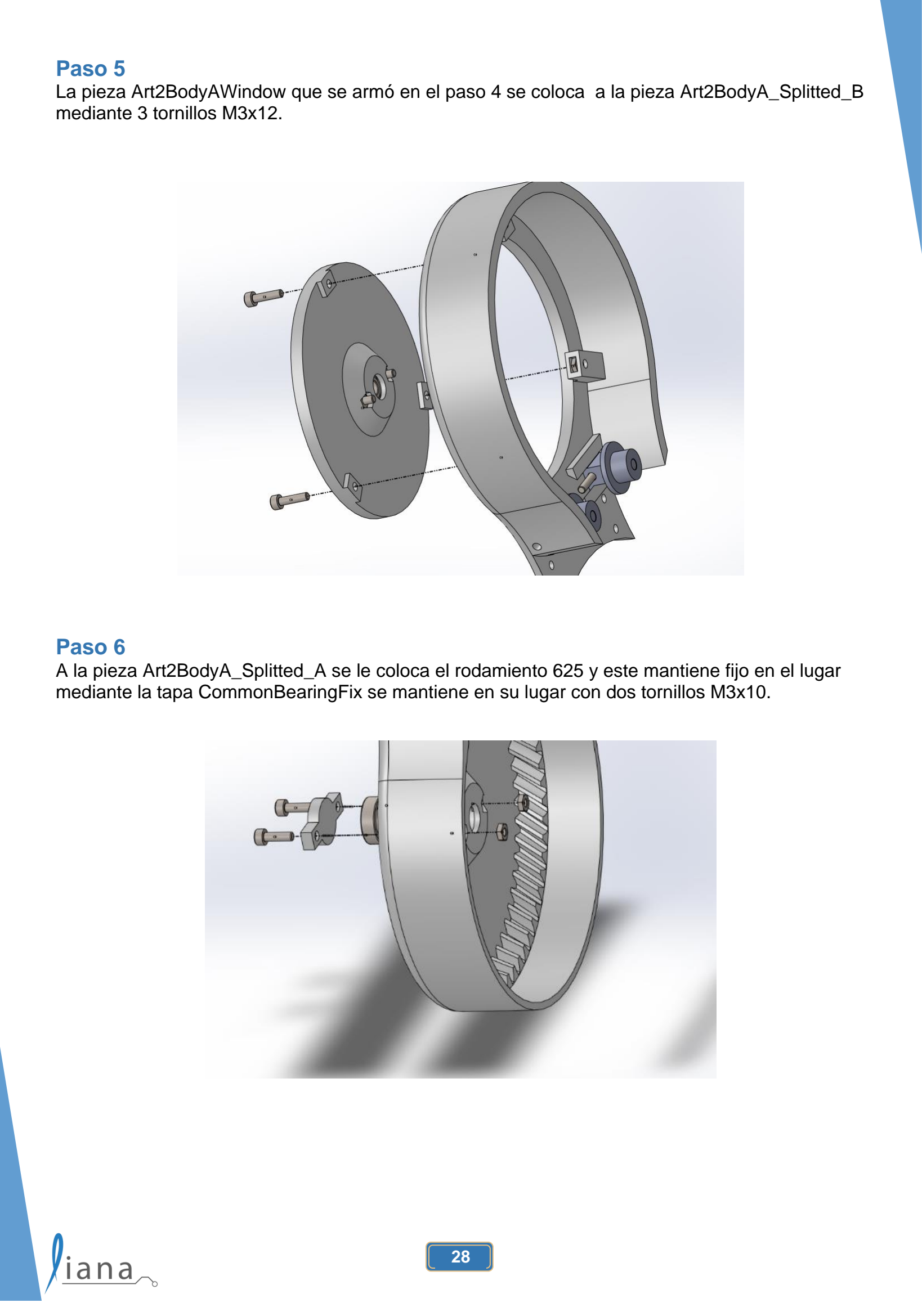
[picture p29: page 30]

28

Paso 5
La pieza Art2BodyAWindow que se armó en el paso 4 se coloca a la pieza Art2BodyA_Splitted_B mediante 3 tornillos M3x12.

Paso 6
A la pieza Art2BodyA_Splitted_A se le coloca el rodamiento 625 y este mantiene fijo en el lugar mediante la tapa CommonBearingFix se mantiene en su lugar con dos tornillos M3x10.

29

Paso 7
Se coloca la pieza Art2BodyA_Splitted_B con la pieza Art2BodyA_Splitted_A y se prensa mediante la pieza Art2BodyACover2 y se fija mediante un tornillo M3x12.

Paso 8
El lado A de la articulación 2 se debe ver de la siguiente forma, se tiene que tener cuidado ya que se puede desarmar o quebrar, es necesario que se termine de unir al lado B de la articulación mediante la unión del medio, pero se hace más adelante.

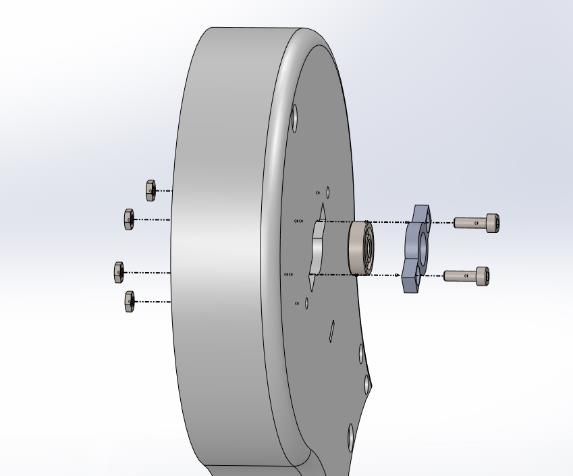
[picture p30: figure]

30

# ARTICULACIÓN 2 LADOB

Paso 1
Este paso se repite para las piezas Art2BodyB_Splitted_A y Art2BodyB_Splitted_B primero se deben colocar 4 tuercas M3 en la parte interna y por la parte externa, se colocan el rodamiento 625 luego se fija mediante la pieza CommonBearingFixThrough y con tornillos M3x10.

Paso 2
Este paso se repite para las piezas Art2BodyB_Splitted_A y Art2BodyB_Splitted_B se colocan 2 tuercas M3 en los cilindros internos, se coloca el final de carrera óptico Lerdge mediante 2 tornillos M3x10.

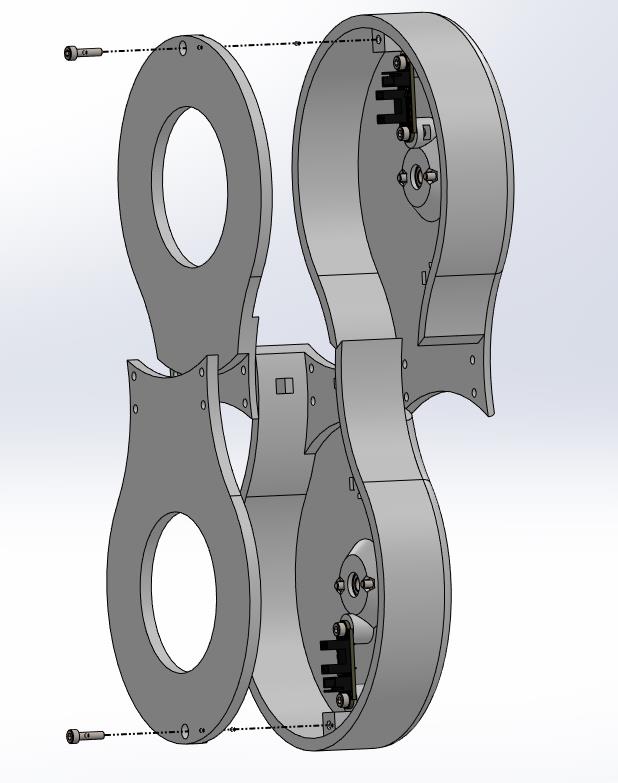
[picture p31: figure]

31

Paso 3
Las piezas se colocan en el orden que se muestra donde primero se coloca Art2BodyB_Splitted_B, luego se coloca Art2BodyB_Splitted_A, se sigue con Art2BodyBCover_Splitted_B y finalmente se coloca Art2BodyBCover_Splitted_A y se asegura mediante 2 tornillos M3x12.

Paso 4
A la pieza Art2BodyUnion se le colocan 8 tuercas M3 como se muestra, en caso de ser necesario se puede agregar un adhesivo para mantenerlas en su lugar.

32

Paso 5
La pieza Art2BodyUnion se una al lado B de la articulación mediante 4 tornillos M3x45.

Paso 6
Este paso se repite para las piezas Art2BodyB_Splitted_A y Art2BodyB_Splitted_B se coloca el enconder siguiendo sus instrucciones de instalación, este paso se debe hacer cuando ya se hayan colocado los ejes. Hay que recordar que si se deben pasar los cables para conectarlos más adelante.

# UNIÓN MEDIA

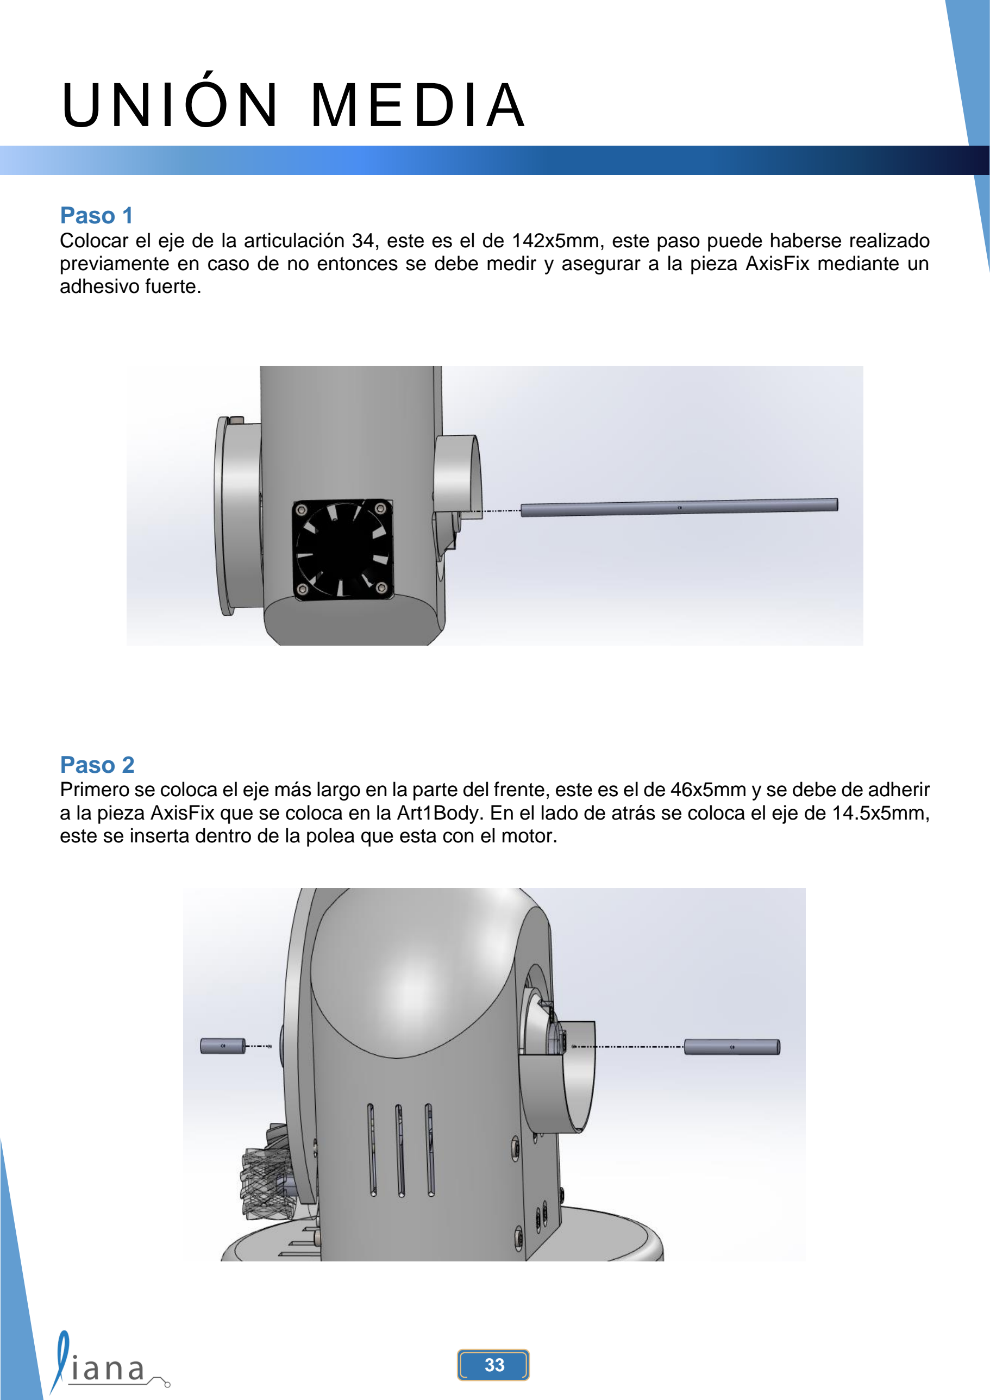
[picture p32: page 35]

33

Paso 1
Colocar el eje de la articulación 34, este es el de 142x5mm, este paso puede haberse realizado previamente en caso de no entonces se debe medir y asegurar a la pieza AxisFix mediante un adhesivo fuerte.

Paso 2
Primero se coloca el eje más largo en la parte del frente, este es el de 46x5mm y se debe de adherir a la pieza AxisFix que se coloca en la Art1Body. En el lado de atrás se coloca el eje de 14.5x5mm, este se inserta dentro de la polea que esta con el motor.

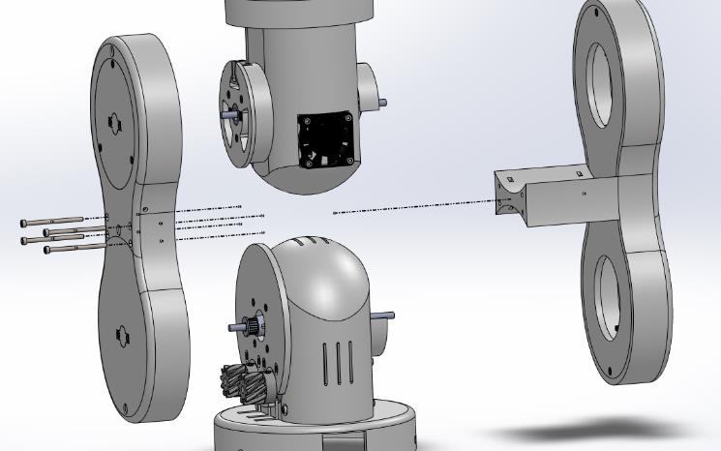
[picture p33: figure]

34

Paso 3
Los lados A y B de la articulación 2 se colocan como se muestra y el lado A es al que se le deben de colocar los 4 tornillos M3x45 para terminar la unión. Después de este paso se deben montar los enconders en el lado B.

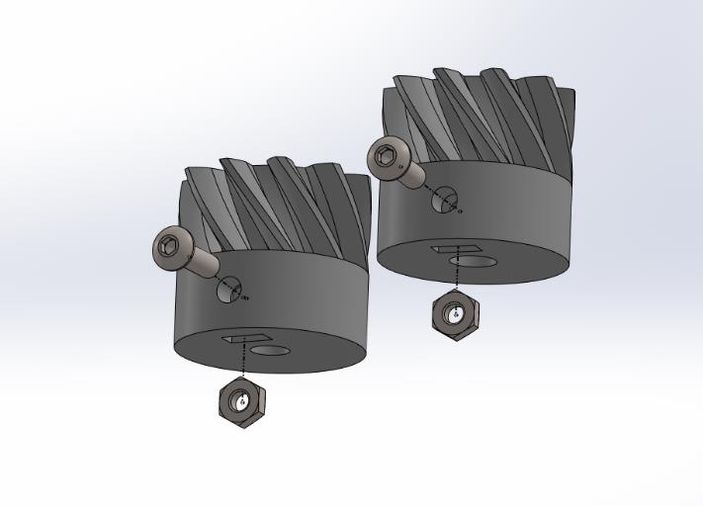
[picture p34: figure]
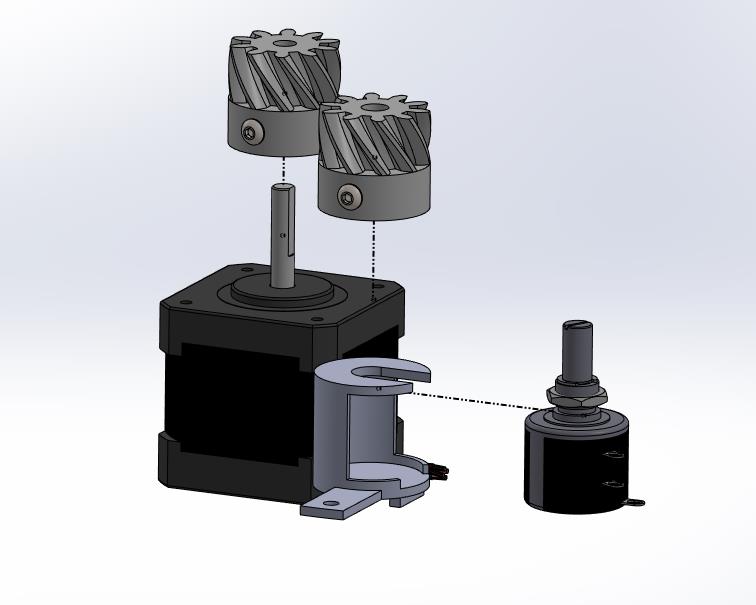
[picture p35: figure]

35

# BASE

Paso 1
A las piezas Art1GearMotor y Art1GearPot se le deben colocar una tuerca M3 con un tornillo M3x10.

Paso 2
La pieza Art1GearMotor se coloca al motor nema17-40 y se asegura con el tornillo, para el potenciómetro este se debe colocar primero en la pieza Art1PotMount y asegurar con la tuerca que este incluye, luego se coloca Art1GearPot y se asegura con su tornillo.

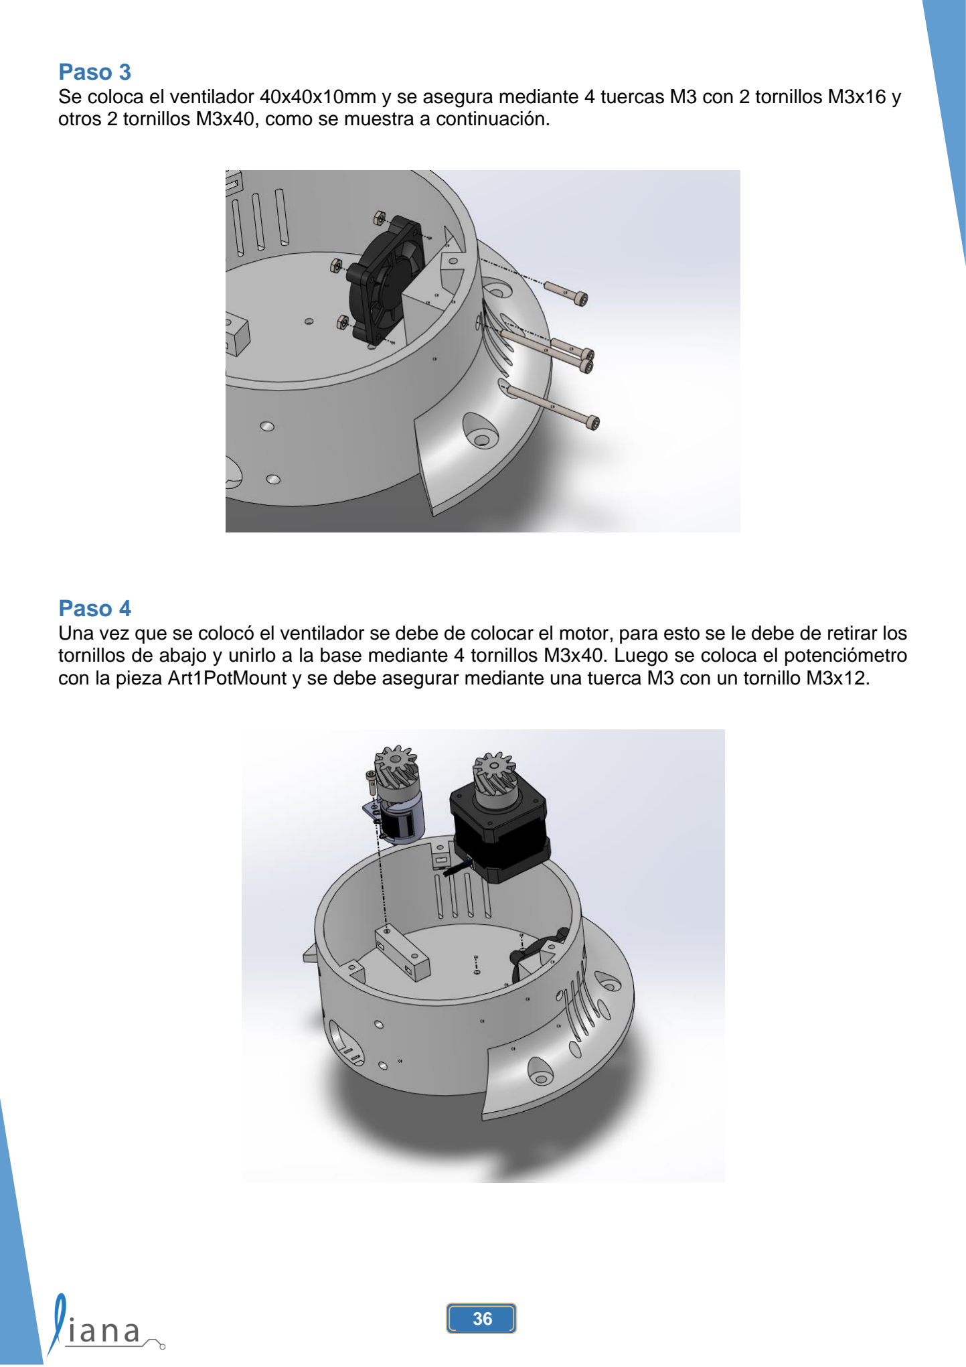
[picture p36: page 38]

36

Paso 3
Se coloca el ventilador 40x40x10mm y se asegura mediante 4 tuercas M3 con 2 tornillos M3x16 y otros 2 tornillos M3x40, como se muestra a continuación.

Paso 4
Una vez que se colocó el ventilador se debe de colocar el motor, para esto se le debe de retirar los tornillos de abajo y unirlo a la base mediante 4 tornillos M3x40. Luego se coloca el potenciómetro con la pieza Art1PotMount y se debe asegurar mediante una tuerca M3 con un tornillo M3x12.

37

Paso 5
Como se indico en el paso 4 el motor nema17-40 mediante 4 tornillos M3x30.

Paso 6
La pieza Art1Bot se le deben colocar 3 tuercas M3 para este si es necesario se deben de asegurar con un adhesivo o similar para facilitar el armado de las piezas.

38

Paso 7
El rodamiento 16014ZZ se coloca por encima de la pieza BaseTop y debajo de este se coloca la pieza Art1Bot.

Paso 8
La pieza BaseTop se coloca debajo de la pieza BaseBearingFix y esta se asegura a la pieza BaseBot mediante 3 tornillos M3x40.

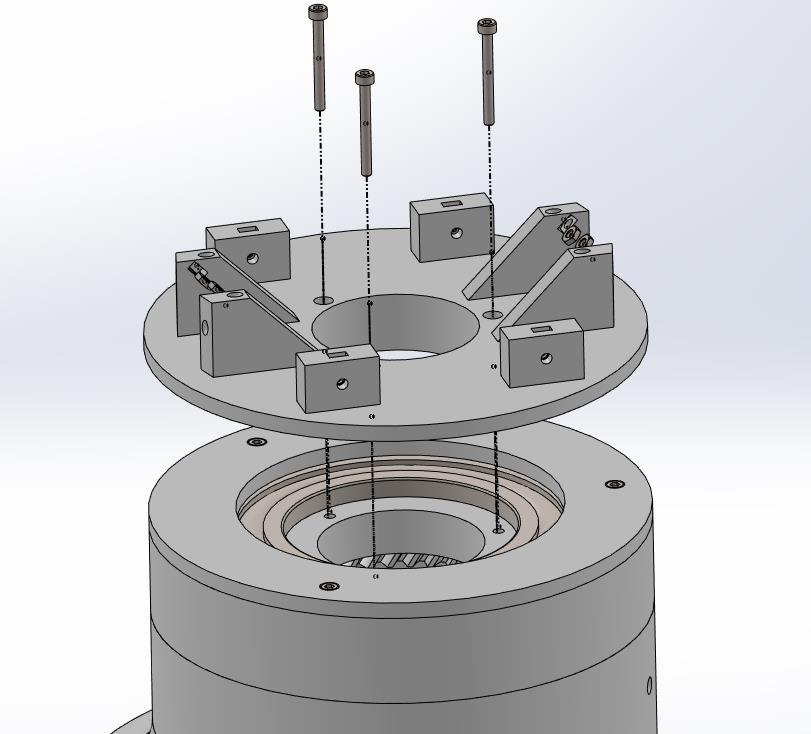
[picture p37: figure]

39

Paso 9
La pieza Art1Top se asegura a la pieza Art1Bot mediante 3 tornillos M3x30 como se muestra a continuación.

Paso 10
A la pieza Art1Top se le colocan 4 tuercas M3 en las aletas o triángulos donde se apoyan los ventiladores.

40

Paso 11
Se colocan 4 tuercas M3 en los rectángulos emergentes laterales.

Paso 12
Se colocan los ventiladores 40x40x10mm sobre la pieza Art1Top.

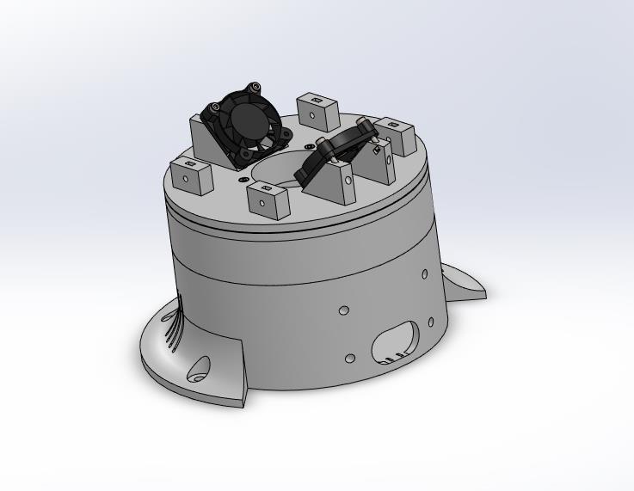
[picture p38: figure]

41

Paso 13
Se aseguran los ventiladores a la pieza Art1Top mediante 4 tornillos M3x20 como se muestra a continuación.

Paso 14
La base se muestra a continuación nada más se debe recordar dejar los tornillos para asegurar le case del PCB.

42

# UNIÓN INFERIOR

Paso 1
La parte superior del brazo se une a la base mediante 4 tornillos M3x16 como se muestra a continuación.

43

# UNIÓN BASE-CASE

Paso 1
Se colocan 10 tuercas M3 en las ranuras mostradas. De ser necesario se pueden fijar con algún tipo de adhesivo, las piezas del case son dos mitades que se deben colocar como se muestra siguiendo las guías que traen.

Paso 2
Mediante 16 tornillos M3x20 se fijan los ventiladores como se muestra, se debe tener en cuenta que 2 deben de meter aire y los otros 2 deben de sacar aire. Se colocan las 16 tuercas M3 respectivas para fijarlos.

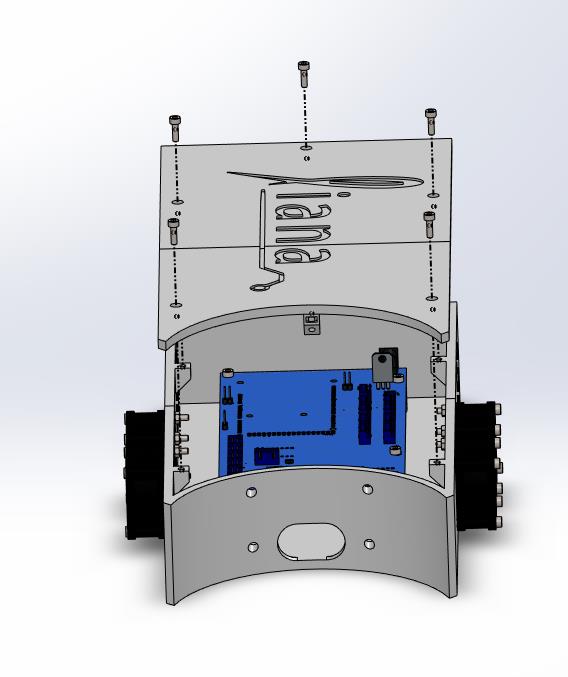
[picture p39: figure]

44

Paso 3
El Arduino se debe de conectar al PCB mediante los pines, luego estos se introducen dentro del case y se alinean los conectores en la salida del case. Finalmente se fijan al case mediante 5 tornillos Mx310.

Paso 4
Antes de cerrar la tapa se debe introducir con mucho cuidado en los 4 tornillos M5x25 que se dejaron en la base, una vez que se metieron se le colocan las tuercas M5 y se asegura el case. Finalmente se cierra la tapa superior mediante 5 tornillos M3x10.

45

Paso 5
Así es como se debería sujeto a la base, ahora solo se muestra la base, pero en la realidad el robot estaría completo. Por eso es por lo que se debe tener mucho cuidado de no meter los tornillos M5 cuando se une el case.

46

# CONEXIÓN ELECTRICA

Ahora se van a presentar las tablas de conexión de los diferentes componentes al Arduino.

Tabla 1. Asignación de los pines de los drivers A4988 al microcontrolador.

Componente | Nombre de señal | Pin de conexión
Motor 6 | Step Dir | 27 29
Motor 5 | Step Dir | 31 33
Motor 4 | Step Dir | 35 37
Motor 3 | Step Dir | 39 41
Motor 2 | Step Dir | 43 45
Motor 1 | Step Dir | 47 49

Tabla 2. Asignación de los pines de los codificadores al microcontrolador.

Componente | Nombre de señal | Pin de conexión
Codificador 6 | Señal A Señal B | 3 2
Codificador 5 | Señal A Señal B | 18 19
Codificador 3 | Señal A Señal B | 20 23
Codificador 2 | Señal A Señal B | 21 25

47

Tabla 3. Asignación de los pines del efector y finales de carrera al microcontrolador.

Componente | Nombre de señal | Pin de conexión
Efector | PWM Señal analógica | 8 A0
Potenciómetro 4 | Señal analógica | A2
Potenciómetro 1 | Señal analógica | A4
Final de carrera 56 | Señal digital | 6
Final óptico 2 | Señal digital | 14
Final óptico 3 | Señal digital | 15

Ahora se van a presentar el PCB con la indicación de cada componente.

- Sención roja: Son las conexiones a los ventiladores, los ventiladores no tienen orden de conexión. Se colocan conectores JST de 2 pines.
- Sección morada: Son la conexión de los drivers y motores, se colocan pines hembra y conectores JST de 4 pines.
- Sección naranja: Son la conexión de los señores y el efector final. Se deben usar conectores JST de 3 y 4 pines.
- Sección café: Corresponde a la alimentación de la tarjeta, se compone por el conector tipo barril DC y el regulador de tensión LM7805.
- Circulo verde: Se colocan pines o se pueden soldar directamente cables para incluir un interruptor de parada de emergencia.

48

Ahora se van a presentar las tablas de codificación de colores. Se asume que rojo y negro son para alimentación de 12V para ventiladores y de 5V para sensores

Tabla 4. Codificación de los colores de los cables.
Componente | Nombre | Color de cable
Codificador | Señal A Señal B | Verde/Amarillo Azul
Codificador PCB | Señal A Señal B | Blanco Gris
Motor a pasos | 1A 1B 2A 2B | Negro Verde Rojo Azul
Efector Final | PWM Señal analógica | Blanco-verde Blanco-naranja
Final carrera 56 | Señal | Blanco/azul
Final óptico | Señal | Blanco
Potenciómetro | Señal | Azul

Tabla 5. Codificación de los cables.
Componente | Nombre de señal | Cantidad de cables
Codificador 6 | ENC6 | 4
Codificador 5 | ENC5 | 4
Codificador 3 | ENC3 | 4
Codificador 2 | ENC2 | 4
Potenciómetro 4 | POT4 | 3
Potenciómetro 1 | POT1 | 3
Final óptico 3 | OPT3 | 3
Final óptico 2 | OPT2 | 3
Final de carrera 56 | FinalC | 2
Efector Final | Efector | 4
Motor articulación 1 | ART1 | 4
Motor articulación 2-1 | ART2_1 | 4
Motor articulación 2-2 | ART_2 | 4
Motor articulación 3 | ART3 | 4
Motor articulación 4 | ART4 | 4
Motor articulación 5 | ART5 | 4
Motor articulación 6 | ART6 | 4

49

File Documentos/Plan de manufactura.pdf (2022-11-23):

# Contenido

## Descripción | 1

## Articulación 56 | 2

## Articulación 34 | 17

## Articulación 2_2 | 27

## Articulación 2_1 | 33

## Articulación 1 | 41

## Base y case del PCB | 45

## Gripper | 58

1

## Descripción

En este documento se encuentra toda la información necesaria para manufacturar cada una de las piezas del manipulador Thor adaptado para ser usado como un componente en el proyecto OSCAR del Laboratorio de inteligencia Artificial para las ciencias naturales LIANA del área académica de mecatrónica en el instituto tecnológico de Costa Rica. No es necesario el uso de hojas de control de calidad ya que las unidades a fabricar son muy pocas, el caso de fabricar seria como repuestos o la fabricación de otro brazo, pero no en masa y para el caso del presupuesto se sabe que el brazo consume alrededor de 3.5Kg en el material de las piezas, los soportes y en caso de fallos, donde el precio de un rollo de 1kg de pla max es de 32 dólares.

Al ser una elevada cantidad de partes se separaron de acuerdo con la parte del brazo a la que pertenecen según como se muestra en la siguiente imagen.

Todos los parámetros son los mismos por lo que se pueden imprimir varias piezas al mismo tiempo solo si estas logran acomodarse dentro del área de trabajo de la impresora en la que se vaya a trabajar y en caso de que la impresora no cuente con el relleno giroide se puede emplear el hexagonal o panal de abeja.

2

## Articulación 56

Todas las piezas que componen la articulación 56 se indican a continuación, como todas las piezas comparten los mismos parámetros se pueden ubicar varias piezas para impresas en el mismo ciclo de trabajo de la impresora, solo que estas se deben de juntar lo más que se pueda para reducir el tiempo de impresión, en caso de necesitar solo una pieza usar la información a continuación.

Lista de las piezas que componen la articulación:

- Art4BearingPlug
- Art4BearingRing
- Art4Body
- Art4BodyBot
- Art4BodyFan
- Art4TransmissionColumn
- Art56GearPlate
- Art56MotorCoverRing
- Art56MotorHolderA
- Art56MotorHolderB
- Art56SmallGear2
- CoverRingBolt
- CoverRingNut
- EncoderMount

3

## Fase de Impresión

No. Parte: | Nombre: Art4BearingPlug | Cliente: LIANA | Material: PLA MAX
Op: 1 Maquina: Impresora 3D Soporte y montaje: N/A | Descripción: Imprimir la pieza y al final retirar el material de soporte u material extra como los hilos que se generan al imprimir. | | Croquis:

## Hoja de proceso

No. Plano: 40 | Nombre: Art4BearingPlug
Gcode: N/A | Maquina: Impresora 3D
Material: PLA MAX
Instrucciones de montaje:
Imprimir la pieza en el centro del área de trabajo.
Op: | Parámetros: | Herramientas | Observaciones:
1 | Resolución de capa: 0,2mm Densidad de relleno: 40% Patrón de relleno: Giroide Imprimir con soportes: Si Temperatura del extrusor: Recomendada para el material | Impresora 3D | El material de soporte no es necesario pues la pieza se diseñó para ser impresa sin este, pero se recomienda su uso para que no se comprometa la calidad e integridad de las piezas.

4

## Fase de Impresión

No. Parte: | Nombre: Art4BearingRing | Cliente: LIANA | Material: PLA MAX
Op: 1 Maquina: Impresora 3D Soporte y montaje: N/A | Descripción: Imprimir la pieza y al final retirar el material de soporte u material extra como los hilos que se generan al imprimir. | | Croquis:

## Hoja de proceso

No. Plano: 41 | Nombre: Art4BearingRing
Gcode: N/A | Maquina: Impresora 3D
Material: PLA MAX
Instrucciones de montaje:
Imprimir la pieza en el centro del área de trabajo.
Op: | Parámetros: | Herramientas | Observaciones:
1 | Resolución de capa: 0,2mm Densidad de relleno: 40% Patrón de relleno: Giroide Imprimir con soportes: Si Temperatura del extrusor: Recomendada para el material | Impresora 3D | El material de soporte no es necesario pues la pieza se diseñó para ser impresa sin este, pero se recomienda su uso para que no se comprometa la calidad e integridad de las piezas.

5

## Fase de Impresión

No. Parte: | Nombre: Art4Body | Cliente: LIANA | Material: PLA MAX
Op: 1 Maquina: Impresora 3D Soporte y montaje: N/A | Descripción: Imprimir la pieza y al final retirar el material de soporte u material extra como los hilos que se generan al imprimir. | | Croquis:

## Hoja de proceso

No. Plano: 42 | Nombre: Art4Body
Gcode: N/A | Maquina: Impresora 3D
Material: PLA MAX
Instrucciones de montaje:
Imprimir la pieza en el centro del área de trabajo.
Op: | Parámetros: | Herramientas | Observaciones:
1 | Resolución de capa: 0,2mm Densidad de relleno: 40% Patrón de relleno: Giroide Imprimir con soportes: Si Temperatura del extrusor: Recomendada para el material | Impresora 3D | El material de soporte no es necesario pues la pieza se diseñó para ser impresa sin este, pero se recomienda su uso para que no se comprometa la calidad e integridad de las piezas.

6

## Fase de Impresión

No. Parte: | Nombre: Art4BodyBot | Cliente: LIANA | Material: PLA MAX
Op: 1 Maquina: Impresora 3D Soporte y montaje: N/A | Descripción: Imprimir la pieza y al final retirar el material de soporte u material extra como los hilos que se generan al imprimir. | | Croquis:

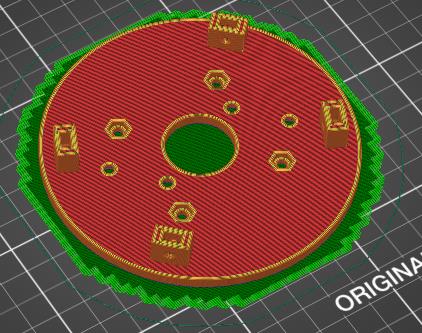
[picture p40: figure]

## Hoja de proceso

No. Plano: 43 | Nombre: Art4BodyBot
Gcode: N/A | Maquina: Impresora 3D
Material: PLA MAX
Instrucciones de montaje:
Imprimir la pieza en el centro del área de trabajo.
Op: | Parámetros: | Herramientas | Observaciones:
1 | Resolución de capa: 0,2mm Densidad de relleno: 40% Patrón de relleno: Giroide Imprimir con soportes: Si Temperatura del extrusor: Recomendada para el material | Impresora 3D

7

## Fase de Impresión

No. Parte: | Nombre: Art4BodyFan | Cliente: LIANA | Material: PLA MAX
Op: 1 Maquina: Impresora 3D Soporte y montaje: N/A | Descripción: Imprimir la pieza y al final retirar el material de soporte u material extra como los hilos que se generan al imprimir. | | Croquis:

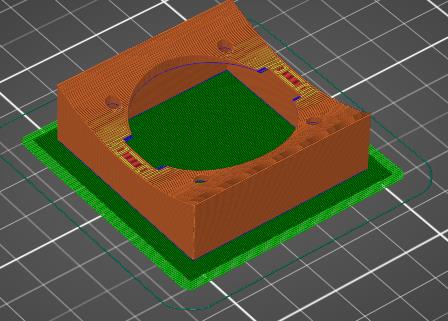
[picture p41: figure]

## Hoja de proceso

No. Plano: 44 | Nombre: Art4BodyFan
Gcode: N/A | Maquina: Impresora 3D
Material: PLA MAX
Instrucciones de montaje:
Imprimir la pieza en el centro del área de trabajo.
Op: | Parámetros: | Herramientas | Observaciones:
1 | Resolución de capa: 0,2mm Densidad de relleno: 40% Patrón de relleno: Giroide Imprimir con soportes: Si Temperatura del extrusor: Recomendada para el material | Impresora 3D | El material de soporte no es necesario pues la pieza se diseñó para ser impresa sin este, pero se recomienda su uso para que no se comprometa la calidad e integridad de las piezas.

8

## Fase de Impresión

No. Parte: | Nombre: Art4TransmissionColumn | Cliente: LIANA | Material: PLA MAX
Op: 1 Maquina: Impresora 3D Soporte y montaje: N/A | Descripción: Imprimir la pieza y al final retirar el material de soporte u material extra como los hilos que se generan al imprimir. | | Croquis:

## Hoja de proceso

No. Plano: 49 | Nombre: Art4TransmissionColumn
Gcode: N/A | Maquina: Impresora 3D
Material: PLA MAX
Instrucciones de montaje:
Imprimir la pieza en el centro del área de trabajo.
Op: | Parámetros: | Herramientas | Observaciones:
1 | Resolución de capa: 0,2mm Densidad de relleno: 40% Patrón de relleno: Giroide Imprimir con soportes: Si Temperatura del extrusor: Recomendada para el material | Impresora 3D | El material de soporte no es necesario pues la pieza se diseñó para ser impresa sin este, pero se recomienda su uso para que no se comprometa la calidad e integridad de las piezas.

9

## Fase de Impresión

No. Parte: | Nombre: Art56GearPlate | Cliente: LIANA | Material: PLA MAX
Op: 1 Maquina: Impresora 3D Soporte y montaje: N/A | Descripción: Imprimir la pieza y al final retirar el material de soporte u material extra como los hilos que se generan al imprimir. | | Croquis:

## Hoja de proceso

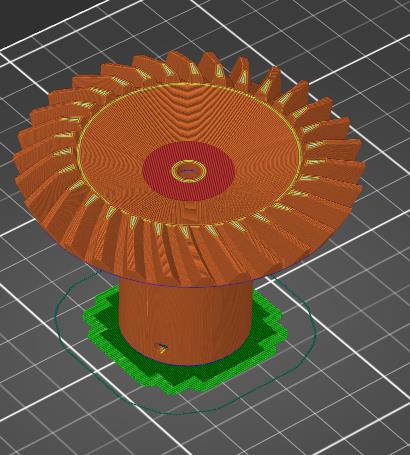
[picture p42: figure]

No. Plano: 50 | Nombre: Art56GearPlate
Gcode: N/A | Maquina: Impresora 3D
Material: PLA MAX
Instrucciones de montaje:
Imprimir la pieza en el centro del área de trabajo.
Op: | Parámetros: | Herramientas | Observaciones:
1 | Resolución de capa: 0,2mm Densidad de relleno: 40% Patrón de relleno: Giroide Imprimir con soportes: Si Temperatura del extrusor: Recomendada para el material | Impresora 3D | El material de soporte no es necesario pues la pieza se diseñó para ser impresa sin este, pero se recomienda su uso para que no se comprometa la calidad e integridad de las piezas.

10

## Fase de Impresión

No. Parte: | Nombre: Art56MotorCoverRing | Cliente: LIANA | Material: PLA MAX
Op: 1 Maquina: Impresora 3D Soporte y montaje: N/A | Descripción: Imprimir la pieza y al final retirar el material de soporte u material extra como los hilos que se generan al imprimir. | | Croquis:

## Hoja de proceso

No. Plano: 51 | Nombre: Art56MotorCoverRing
Gcode: N/A | Maquina: Impresora 3D
Material: PLA MAX
Instrucciones de montaje:
Imprimir la pieza en el centro del área de trabajo.
Op: | Parámetros: | Herramientas | Observaciones:
1 | Resolución de capa: 0,2mm Densidad de relleno: 40% Patrón de relleno: Giroide Imprimir con soportes: Si Temperatura del extrusor: Recomendada para el material | Impresora 3D | El material de soporte no es necesario pues la pieza se diseñó para ser impresa sin este, pero se recomienda su uso para que no se comprometa la calidad e integridad de las piezas.

11

## Fase de Impresión

No. Parte: | Nombre: Art56MotorHolderA | Cliente: LIANA | Material: PLA MAX
Op: 1 Maquina: Impresora 3D Soporte y montaje: N/A | Descripción: Imprimir la pieza y al final retirar el material de soporte u material extra como los hilos que se generan al imprimir. | | Croquis:

## Hoja de proceso

No. Plano: 52 | Nombre: Art56MotorHolderA
Gcode: N/A | Maquina: Impresora 3D
Material: PLA MAX
Instrucciones de montaje:
Imprimir la pieza en el centro del área de trabajo.
Op: | Parámetros: | Herramientas | Observaciones:
1 | Resolución de capa: 0,2mm Densidad de relleno: 40% Patrón de relleno: Giroide Imprimir con soportes: Si Temperatura del extrusor: Recomendada para el material | Impresora 3D | El material de soporte no es necesario pues la pieza se diseñó para ser impresa sin este, pero se recomienda su uso para que no se comprometa la calidad e integridad de las piezas.

12

## Fase de Impresión

No. Parte: | Nombre: Art56MotorHolderB | Cliente: LIANA | Material: PLA MAX
Op: 1 Maquina: Impresora 3D Soporte y montaje: N/A | Descripción: Imprimir la pieza y al final retirar el material de soporte u material extra como los hilos que se generan al imprimir. | | Croquis:

## Hoja de proceso

No. Plano: 53 | Nombre: Art56MotorHolderB
Gcode: N/A | Maquina: Impresora 3D
Material: PLA MAX
Instrucciones de montaje:
Imprimir la pieza en el centro del área de trabajo.
Op: | Parámetros: | Herramientas | Observaciones:
1 | Resolución de capa: 0,2mm Densidad de relleno: 40% Patrón de relleno: Giroide Imprimir con soportes: Si Temperatura del extrusor: Recomendada para el material | Impresora 3D | El material de soporte no es necesario pues la pieza se diseñó para ser impresa sin este, pero se recomienda su uso para que no se comprometa la calidad e integridad de las piezas.

13

## Fase de Impresión

No. Parte: | Nombre: Art56SmallGear | Cliente: LIANA | Material: PLA MAX
Op: 1 Maquina: Impresora 3D Soporte y montaje: N/A | Descripción: Imprimir la pieza y al final retirar el material de soporte u material extra como los hilos que se generan al imprimir. | | Croquis:

## Hoja de proceso

No. Plano: 54 | Nombre: Art56SmallGear
Gcode: N/A | Maquina: Impresora 3D
Material: PLA MAX
Instrucciones de montaje:
Imprimir la pieza en el centro del área de trabajo.
Op: | Parámetros: | Herramientas | Observaciones:
1 | Resolución de capa: 0,2mm Densidad de relleno: 40% Patrón de relleno: Giroide Imprimir con soportes: Si Temperatura del extrusor: Recomendada para el material | Impresora 3D | El material de soporte no es necesario pues la pieza se diseñó para ser impresa sin este, pero se recomienda su uso para que no se comprometa la calidad e integridad de las piezas.

14

## Fase de Impresión

No. Parte: | Nombre: CoverRingBolt | Cliente: LIANA | Material: PLA MAX
Op: 1 Maquina: Impresora 3D Soporte y montaje: N/A | Descripción: Imprimir la pieza y al final retirar el material de soporte u material extra como los hilos que se generan al imprimir. | | Croquis:

## Hoja de proceso

No. Plano: 55 | Nombre: CoverRingBolt
Gcode: N/A | Maquina: Impresora 3D
Material: PLA MAX
Instrucciones de montaje:
Imprimir la pieza en el centro del área de trabajo.
Op: | Parámetros: | Herramientas | Observaciones:
1 | Resolución de capa: 0,2mm Densidad de relleno: 40% Patrón de relleno: Giroide Imprimir con soportes: Si Temperatura del extrusor: Recomendada para el material | Impresora 3D

15

## Fase de Impresión

No. Parte: | Nombre: CoverRingNut | Cliente: LIANA | Material: PLA MAX
Op: 1 Maquina: Impresora 3D Soporte y montaje: N/A | Descripción: Imprimir la pieza y al final retirar el material de soporte u material extra como los hilos que se generan al imprimir. | | Croquis:

## Hoja de proceso

No. Plano: 56 | Nombre: CoverRingNut
Gcode: N/A | Maquina: Impresora 3D
Material: PLA MAX
Instrucciones de montaje:
Imprimir la pieza en el centro del área de trabajo.
Op: | Parámetros: | Herramientas | Observaciones:
1 | Resolución de capa: 0,2mm Densidad de relleno: 40% Patrón de relleno: Giroide Imprimir con soportes: Si Temperatura del extrusor: Recomendada para el material | Impresora 3D

16

## Fase de Impresión

No. Parte: | Nombre: EncoderMount | Cliente: LIANA | Material: PLA MAX
Op: 1 Maquina: Impresora 3D Soporte y montaje: N/A | Descripción: Imprimir la pieza y al final retirar el material de soporte u material extra como los hilos que se generan al imprimir. | | Croquis:

## Hoja de proceso

No. Plano: 71 | Nombre: EncoderMount
Gcode: N/A | Maquina: Impresora 3D
Material: PLA MAX
Instrucciones de montaje:
Imprimir la pieza en el centro del área de trabajo.
Op: | Parámetros: | Herramientas | Observaciones:
1 | Resolución de capa: 0,2mm Densidad de relleno: 40% Patrón de relleno: Giroide Imprimir con soportes: Si Temperatura del extrusor: Recomendada para el material | Impresora 3D

17

## Articulación 34

Todas las piezas que componen la articulación 34 se indican a continuación, como todas las piezas comparten los mismos parámetros se pueden ubicar varias piezas para impresas en el mismo ciclo de trabajo de la impresora, solo que estas se deben de juntar lo más que se pueda para reducir el tiempo de impresión, en caso de necesitar solo una pieza usar la información a continuación.

Lista de las piezas que componen la articulación:

- Art3Body
- Art3Pulley
- Art4MotorFix
- Art4MotorGear
- Art4PotGear
- Art4MotorMount
- Art23Optodisk
- AxisFix
- CommonBearingFixThroug

18

## Fase de Impresión

No. Parte: | Nombre: Art3Body | Cliente: LIANA | Material: PLA MAX
Op: 1 Maquina: Impresora 3D Soporte y montaje: N/A | Descripción: Imprimir la pieza y al final retirar el material de soporte u material extra como los hilos que se generan al imprimir. | | Croquis:

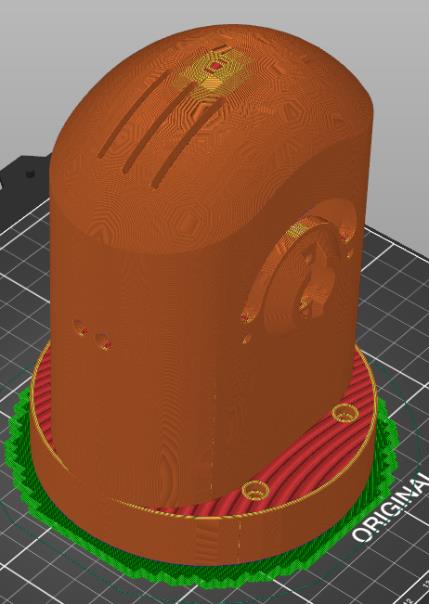
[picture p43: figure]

## Hoja de proceso

No. Plano: 35 | Nombre: Art3Body
Gcode: N/A | Maquina: Impresora 3D
Material: PLA MAX
Instrucciones de montaje:
Imprimir la pieza en el centro del área de trabajo.
Op: | Parámetros: | Herramientas | Observaciones:
1 | Resolución de capa: 0,2mm Densidad de relleno: 40% Patrón de relleno: Giroide Imprimir con soportes: Si Temperatura del extrusor: Recomendada para el material | Impresora 3D | El material de soporte no es necesario pues la pieza se diseñó para ser impresa sin este, pero se recomienda su uso para que no se comprometa la calidad e integridad de las piezas.

19

## Fase de Impresión

No. Parte: | Nombre: Art3Pulley | Cliente: LIANA | Material: PLA MAX
Op: 1 Maquina: Impresora 3D Soporte y montaje: N/A | Descripción: Imprimir la pieza y al final retirar el material de soporte u material extra como los hilos que se generan al imprimir. | | Croquis:

## Hoja de proceso

No. Plano: 36 | Nombre: Art3Pulley
Gcode: N/A | Maquina: Impresora 3D
Material: PLA MAX
Instrucciones de montaje:
Imprimir la pieza en el centro del área de trabajo.
Op: | Parámetros: | Herramientas | Observaciones:
1 | Resolución de capa: 0,2mm Densidad de relleno: 40% Patrón de relleno: Giroide Imprimir con soportes: Si Temperatura del extrusor: Recomendada para el material | Impresora 3D | El material de soporte no es necesario pues la pieza se diseñó para ser impresa sin este, pero se recomienda su uso para que no se comprometa la calidad e integridad de las piezas.

20

## Fase de Impresión

No. Parte: | Nombre: Art4MotorFix | Cliente: LIANA | Material: PLA MAX
Op: 1 Maquina: Impresora 3D Soporte y montaje: N/A | Descripción: Imprimir la pieza y al final retirar el material de soporte u material extra como los hilos que se generan al imprimir. | | Croquis:

## Hoja de proceso

No. Plano: 45 | Nombre: Art4MotorFix
Gcode: N/A | Maquina: Impresora 3D
Material: PLA MAX
Instrucciones de montaje:
Imprimir la pieza en el centro del área de trabajo.
Op: | Parámetros: | Herramientas | Observaciones:
1 | Resolución de capa: 0,2mm Densidad de relleno: 40% Patrón de relleno: Giroide Imprimir con soportes: Si Temperatura del extrusor: Recomendada para el material | Impresora 3D

21

## Fase de Impresión

No. Parte: | Nombre: Art4MotorGear | Cliente: LIANA | Material: PLA MAX
Op: 1 Maquina: Impresora 3D Soporte y montaje: N/A | Descripción: Imprimir la pieza y al final retirar el material de soporte u material extra como los hilos que se generan al imprimir. | | Croquis:

## Hoja de proceso

No. Plano: 46 | Nombre: Art4MotorGear
Gcode: N/A | Maquina: Impresora 3D
Material: PLA MAX
Instrucciones de montaje:
Imprimir la pieza en el centro del área de trabajo.
Op: | Parámetros: | Herramientas | Observaciones:
1 | Resolución de capa: 0,2mm Densidad de relleno: 40% Patrón de relleno: Giroide Imprimir con soportes: Si Temperatura del extrusor: Recomendada para el material | Impresora 3D

22

## Fase de Impresión

No. Parte: | Nombre: Art4PotGear | Cliente: LIANA | Material: PLA MAX
Op: 1 Maquina: Impresora 3D Soporte y montaje: N/A | Descripción: Imprimir la pieza y al final retirar el material de soporte u material extra como los hilos que se generan al imprimir. | | Croquis:

## Hoja de proceso

No. Plano: 47 | Nombre: Art4PotGear
Gcode: N/A | Maquina: Impresora 3D
Material: PLA MAX
Instrucciones de montaje:
Imprimir la pieza en el centro del área de trabajo.
Op: | Parámetros: | Herramientas | Observaciones:
1 | Resolución de capa: 0,2mm Densidad de relleno: 40% Patrón de relleno: Giroide Imprimir con soportes: Si Temperatura del extrusor: Recomendada para el material | Impresora 3D

23

## Fase de Impresión

No. Parte: | Nombre: Art4PotMount | Cliente: LIANA | Material: PLA MAX
Op: 1 Maquina: Impresora 3D Soporte y montaje: N/A | Descripción: Imprimir la pieza y al final retirar el material de soporte u material extra como los hilos que se generan al imprimir. | | Croquis:

## Hoja de proceso

No. Plano: 48 | Nombre: Art4PotMount
Gcode: N/A | Maquina: Impresora 3D
Material: PLA MAX
Instrucciones de montaje:
Imprimir la pieza en el centro del área de trabajo.
Op: | Parámetros: | Herramientas | Observaciones:
1 | Resolución de capa: 0,2mm Densidad de relleno: 40% Patrón de relleno: Giroide Imprimir con soportes: Si Temperatura del extrusor: Recomendada para el material | Impresora 3D

24

## Fase de Impresión

No. Parte: | Nombre: Art23Optodisk | Cliente: LIANA | Material: PLA MAX
Op: 1 Maquina: Impresora 3D Soporte y montaje: N/A | Descripción: Imprimir la pieza y al final retirar el material de soporte u material extra como los hilos que se generan al imprimir. | | Croquis:

## Hoja de proceso

No. Plano: 39 | Nombre: Art4BearingPlug
Gcode: N/A | Maquina: Impresora 3D
Material: PLA MAX
Instrucciones de montaje:
Imprimir la pieza en el centro del área de trabajo.
Op: | Parámetros: | Herramientas | Observaciones:
1 | Resolución de capa: 0,2mm Densidad de relleno: 40% Patrón de relleno: Giroide Imprimir con soportes: Si Temperatura del extrusor: Recomendada para el material | Impresora 3D

25

## Fase de Impresión

No. Parte: | Nombre: AxisFix | Cliente: LIANA | Material: PLA MAX
Op: 1 Maquina: Impresora 3D Soporte y montaje: N/A | Descripción: Imprimir la pieza y al final retirar el material de soporte u material extra como los hilos que se generan al imprimir. | | Croquis:

## Hoja de proceso

No. Plano: 68 | Nombre: Art4BearingPlug
Gcode: N/A | Maquina: Impresora 3D
Material: PLA MAX
Instrucciones de montaje:
Imprimir la pieza en el centro del área de trabajo.
Op: | Parámetros: | Herramientas | Observaciones:
1 | Resolución de capa: 0,2mm Densidad de relleno: 40% Patrón de relleno: Giroide Imprimir con soportes: Si Temperatura del extrusor: Recomendada para el material | Impresora 3D | El material de soporte no es necesario pues la pieza se diseñó para ser impresa sin este, pero se recomienda su uso para que no se comprometa la calidad e integridad de las piezas.

26

## Fase de Impresión

No. Parte: | Nombre: CommonBearing FixThrough | Cliente: LIANA | Material: PLA MAX
Op: 1 Maquina: Impresora 3D Soporte y montaje: N/A | Descripción: Imprimir la pieza y al final retirar el material de soporte u material extra como los hilos que se generan al imprimir. | | Croquis:

## Hoja de proceso

No. Plano: 70 | Nombre: CommonBearingFixThrough
Gcode: N/A | Maquina: Impresora 3D
Material: PLA MAX
Instrucciones de montaje:
Imprimir la pieza en el centro del área de trabajo.
Op: | Parámetros: | Herramientas | Observaciones:
1 | Resolución de capa: 0,2mm Densidad de relleno: 40% Patrón de relleno: Giroide Imprimir con soportes: Si Temperatura del extrusor: Recomendada para el material | Impresora 3D

27

## Articulación 2_2

Todas las piezas que componen la articulación 2_2 se indican a continuación, como todas las piezas comparten los mismos parámetros se pueden ubicar varias piezas para impresas en el mismo ciclo de trabajo de la impresora, solo que estas se deben de juntar lo más que se pueda para reducir el tiempo de impresión, en caso de necesitar solo una pieza usar la información a continuación.

Lista de las piezas que componen la articulación:

- Art2BodyB_Splitted_A
- Art2BodyB_Splitted_B
- Art2BodyBCover_Splitted_A
- Art2BodyBCover_Splitted_B
- Art2BodyUnion
- CommonBearingFixThrough (ya se indicó en articulación 34)

28

## Fase de Impresión

No. Parte: | Nombre: Art2BodyB_Splitted_A | Cliente: LIANA | Material: PLA MAX
Op: 1 Maquina: Impresora 3D Soporte y montaje: N/A | Descripción: Imprimir la pieza y al final retirar el material de soporte u material extra como los hilos que se generan al imprimir. | | Croquis:

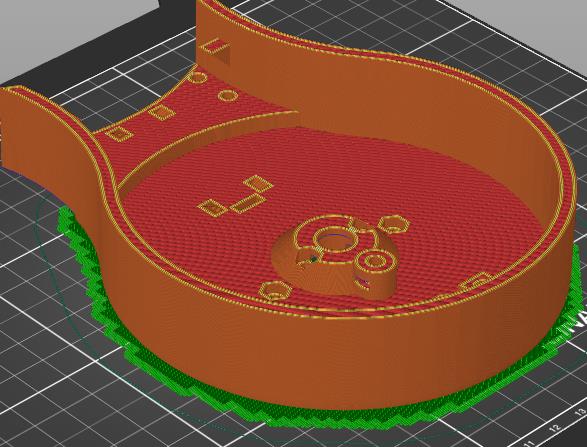
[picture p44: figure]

## Hoja de proceso

No. Plano: 29 | Nombre: Art2BodyB_Splitted_A
Gcode: N/A | Maquina: Impresora 3D
Material: PLA MAX
Instrucciones de montaje:
Imprimir la pieza en el centro del área de trabajo.
Op: | Parámetros: | Herramientas | Observaciones:
1 | Resolución de capa: 0,2mm Densidad de relleno: 40% Patrón de relleno: Giroide Imprimir con soportes: Si Temperatura del extrusor: Recomendada para el material | Impresora 3D | El material de soporte no es necesario pues la pieza se diseñó para ser impresa sin este, pero se recomienda su uso para que no se comprometa la calidad e integridad de las piezas.

29

## Fase de Impresión

No. Parte: | Nombre: Art2BodyB_Splitted_B | Cliente: LIANA | Material: PLA MAX
Op: 1 Maquina: Impresora 3D Soporte y montaje: N/A | Descripción: Imprimir la pieza y al final retirar el material de soporte u material extra como los hilos que se generan al imprimir. | | Croquis:

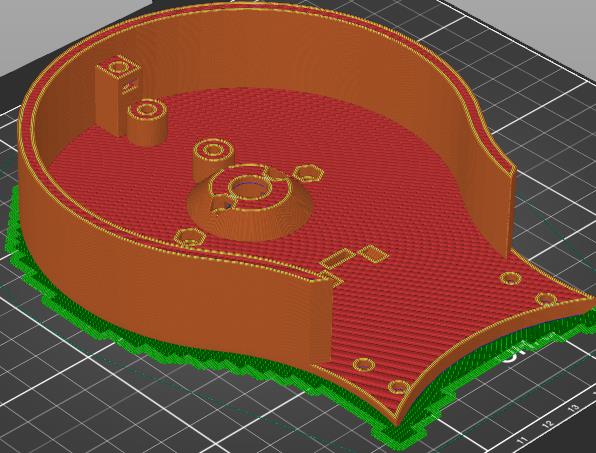
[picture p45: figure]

## Hoja de proceso

No. Plano: 30 | Nombre: Art2BodyB_Splitted_B
Gcode: N/A | Maquina: Impresora 3D
Material: PLA MAX
Instrucciones de montaje:
Imprimir la pieza en el centro del área de trabajo.
Op: | Parámetros: | Herramientas | Observaciones:
1 | Resolución de capa: 0,2mm Densidad de relleno: 40% Patrón de relleno: Giroide Imprimir con soportes: Si Temperatura del extrusor: Recomendada para el material | Impresora 3D | El material de soporte no es necesario pues la pieza se diseñó para ser impresa sin este, pero se recomienda su uso para que no se comprometa la calidad e integridad de las piezas.

30

## Fase de Impresión

No. Parte: | Nombre: Art2BodyBCover Splitted_A | Cliente: LIANA | Material: PLA MAX
Op: 1 Maquina: Impresora 3D Soporte y montaje: N/A | Descripción: Imprimir la pieza y al final retirar el material de soporte u material extra como los hilos que se generan al imprimir. | | Croquis:

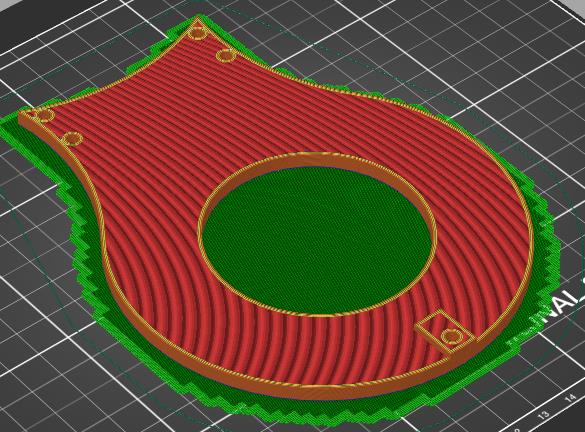
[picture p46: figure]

## Hoja de proceso

No. Plano: 31 | Nombre: Art2BodyBCover_Splitted_A
Gcode: N/A | Maquina: Impresora 3D
Material: PLA MAX
Instrucciones de montaje:
Imprimir la pieza en el centro del área de trabajo.
Op: | Parámetros: | Herramientas | Observaciones:
1 | Resolución de capa: 0,2mm Densidad de relleno: 40% Patrón de relleno: Giroide Imprimir con soportes: Si Temperatura del extrusor: Recomendada para el material | Impresora 3D | El material de soporte no es necesario pues la pieza se diseñó para ser impresa sin este, pero se recomienda su uso para que no se comprometa la calidad e integridad de las piezas.

31

## Fase de Impresión

No. Parte: | Nombre: Art2BodyBCover Splitted_B | Cliente: LIANA | Material: PLA MAX
Op: 1 Maquina: Impresora 3D Soporte y montaje: N/A | Descripción: Imprimir la pieza y al final retirar el material de soporte u material extra como los hilos que se generan al imprimir. | | Croquis:

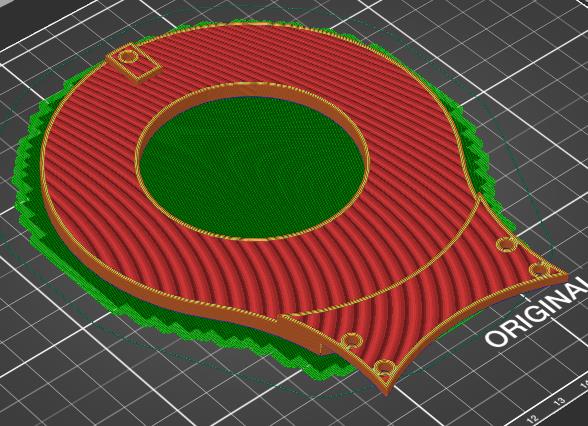
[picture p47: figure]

## Hoja de proceso

No. Plano: 32 | Nombre: Art2BodyBCover_Splitted_B
Gcode: N/A | Maquina: Impresora 3D
Material: PLA MAX
Instrucciones de montaje:
Imprimir la pieza en el centro del área de trabajo.
Op: | Parámetros: | Herramientas | Observaciones:
1 | Resolución de capa: 0,2mm Densidad de relleno: 40% Patrón de relleno: Giroide Imprimir con soportes: Si Temperatura del extrusor: Recomendada para el material | Impresora 3D | El material de soporte no es necesario pues la pieza se diseñó para ser impresa sin este, pero se recomienda su uso para que no se comprometa la calidad e integridad de las piezas.

32

## Fase de Impresión

No. Parte: | Nombre: Art2BodyUnion | Cliente: LIANA | Material: PLA MAX
Op: 1 Maquina: Impresora 3D Soporte y montaje: N/A | Descripción: Imprimir la pieza y al final retirar el material de soporte u material extra como los hilos que se generan al imprimir. | | Croquis:

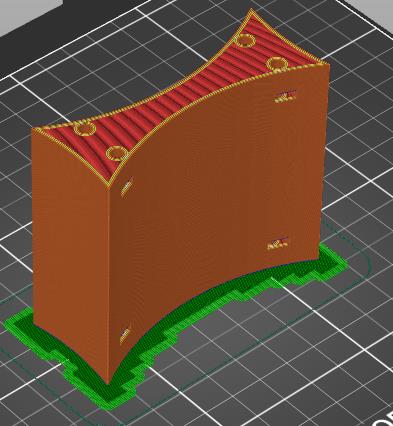
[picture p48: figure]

## Hoja de proceso

No. Plano: 33 | Nombre: Art2BodyUnion
Gcode: N/A | Maquina: Impresora 3D
Material: PLA MAX
Instrucciones de montaje:
Imprimir la pieza en el centro del área de trabajo.
Op: | Parámetros: | Herramientas | Observaciones:
1 | Resolución de capa: 0,2mm Densidad de relleno: 40% Patrón de relleno: Giroide Imprimir con soportes: Si Temperatura del extrusor: Recomendada para el material | Impresora 3D

33

## Articulación 2_1

Todas las piezas que componen la articulación 2_1 se indican a continuación, como todas las piezas comparten los mismos parámetros se pueden ubicar varias piezas para impresas en el mismo ciclo de trabajo de la impresora, solo que estas se deben de juntar lo más que se pueda para reducir el tiempo de impresión, en caso de necesitar solo una pieza usar la información a continuación.

Lista de las piezas que componen la articulación:

- Art2BodyA_Splitted_A
- Art2BodyA_Splitted_B
- Art2BodyACover2
- Art2BodyAWindow
- Art3TensionerBody
- Art3TensionerPulley
- CommonBearingFix

34

## Fase de Impresión

No. Parte: | Nombre: Art2BodyA_Splitted_A | Cliente: LIANA | Material: PLA MAX
Op: 1 Maquina: Impresora 3D Soporte y montaje: N/A | Descripción: Imprimir la pieza y al final retirar el material de soporte u material extra como los hilos que se generan al imprimir. | | Croquis:

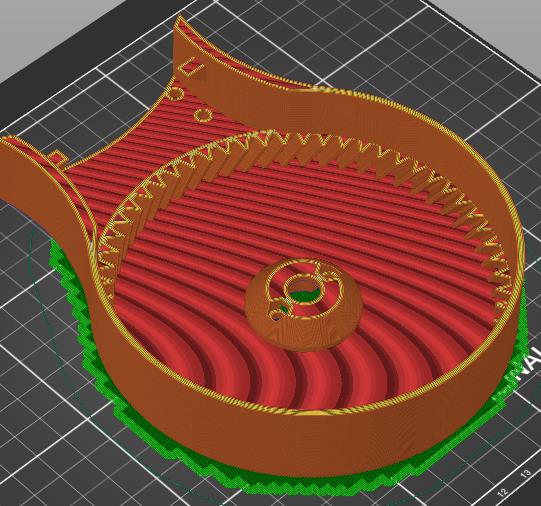
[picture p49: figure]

## Hoja de proceso

No. Plano: 24 | Nombre: Art2BodyA_Splitted_A
Gcode: N/A | Maquina: Impresora 3D
Material: PLA MAX
Instrucciones de montaje:
Imprimir la pieza en el centro del área de trabajo.
Op: | Parámetros: | Herramientas | Observaciones:
1 | Resolución de capa: 0,2mm Densidad de relleno: 40% Patrón de relleno: Giroide Imprimir con soportes: Si Temperatura del extrusor: Recomendada para el material | Impresora 3D | El material de soporte no es necesario pues la pieza se diseñó para ser impresa sin este, pero se recomienda su uso para que no se comprometa la calidad e integridad de las piezas.

35

## Fase de Impresión

No. Parte: | Nombre: Art2BodyA_Splitted_B | Cliente: LIANA | Material: PLA MAX
Op: 1 Maquina: Impresora 3D Soporte y montaje: N/A | Descripción: Imprimir la pieza y al final retirar el material de soporte u material extra como los hilos que se generan al imprimir. | | Croquis:

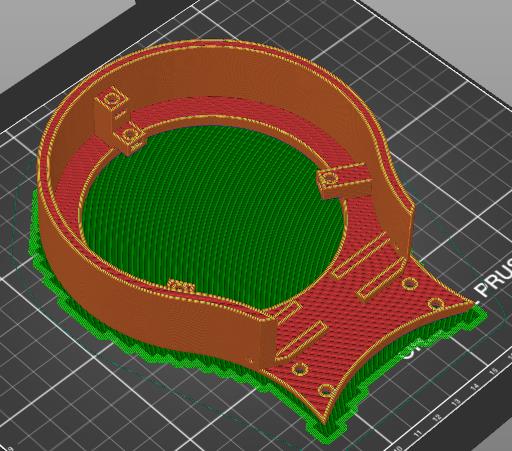
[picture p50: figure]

## Hoja de proceso

No. Plano: 25 | Nombre: Art2BodyA_Splitted_B
Gcode: N/A | Maquina: Impresora 3D
Material: PLA MAX
Instrucciones de montaje:
Imprimir la pieza en el centro del área de trabajo.
Op: | Parámetros: | Herramientas | Observaciones:
1 | Resolución de capa: 0,2mm Densidad de relleno: 40% Patrón de relleno: Giroide Imprimir con soportes: Si Temperatura del extrusor: Recomendada para el material | Impresora 3D | El material de soporte no es necesario pues la pieza se diseñó para ser impresa sin este, pero se recomienda su uso para que no se comprometa la calidad e integridad de las piezas.

36

## Fase de Impresión

No. Parte: | Nombre: Art2BodyACover2 | Cliente: LIANA | Material: PLA MAX
Op: 1 Maquina: Impresora 3D Soporte y montaje: N/A | Descripción: Imprimir la pieza y al final retirar el material de soporte u material extra como los hilos que se generan al imprimir. | | Croquis:

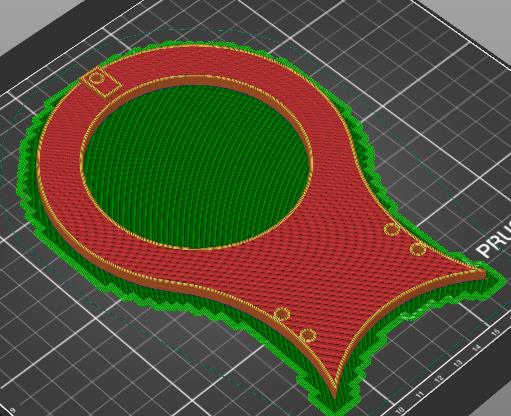
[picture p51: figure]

## Hoja de proceso

No. Plano: 27

Nombre:
Art2BodyACover2
Gcode: N/A | Maquina: Impresora 3D
Material: PLA MAX
Instrucciones de montaje:
Imprimir la pieza en el centro del área de trabajo.
Op: | Parámetros: | Herramientas | Observaciones:
1 | Resolución de capa: 0,2mm Densidad de relleno: 40% Patrón de relleno: Giroide Imprimir con soportes: Si Temperatura del extrusor: Recomendada para el material | Impresora 3D | El material de soporte no es necesario pues la pieza se diseñó para ser impresa sin este, pero se recomienda su uso para que no se comprometa la calidad e integridad de las piezas.

37

## Fase de Impresión

No. Parte: | Nombre: Art2BodyAWindow | Cliente: LIANA | Material: PLA MAX
Op: 1 Maquina: Impresora 3D Soporte y montaje: N/A | Descripción: Imprimir la pieza y al final retirar el material de soporte u material extra como los hilos que se generan al imprimir. | | Croquis:

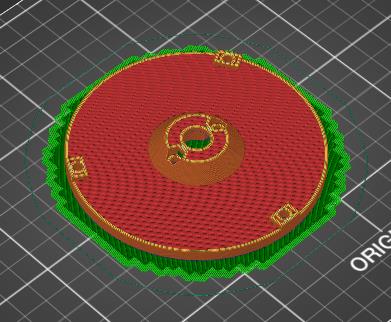
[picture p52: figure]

## Hoja de proceso

No. Plano: 28 | Nombre: Art2BodyAWindow
Gcode: N/A | Maquina: Impresora 3D
Material: PLA MAX
Instrucciones de montaje:
Imprimir la pieza en el centro del área de trabajo.
Op: | Parámetros: | Herramientas | Observaciones:
1 | Resolución de capa: 0,2mm Densidad de relleno: 40% Patrón de relleno: Giroide Imprimir con soportes: Si Temperatura del extrusor: Recomendada para el material | Impresora 3D | El material de soporte no es necesario pues la pieza se diseñó para ser impresa sin este, pero se recomienda su uso para que no se comprometa la calidad e integridad de las piezas.

38

## Fase de Impresión

No. Parte: | Nombre: Art3TensionerBody | Cliente: LIANA | Material: PLA MAX
Op: 1 Maquina: Impresora 3D Soporte y montaje: N/A | Descripción: Imprimir la pieza y al final retirar el material de soporte u material extra como los hilos que se generan al imprimir. | | Croquis:

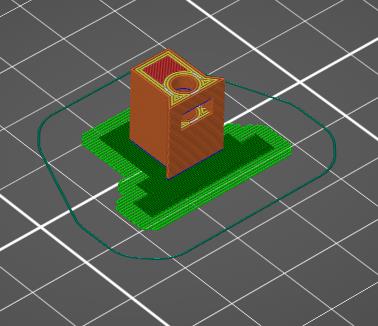
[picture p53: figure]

## Hoja de proceso

No. Plano: 37 | Nombre: Art3TensionerBody
Gcode: N/A | Maquina: Impresora 3D
Material: PLA MAX
Instrucciones de montaje:
Imprimir la pieza en el centro del área de trabajo.
Op: | Parámetros: | Herramientas | Observaciones:
1 | Resolución de capa: 0,2mm Densidad de relleno: 40% Patrón de relleno: Giroide Imprimir con soportes: Si Temperatura del extrusor: Recomendada para el material | Impresora 3D | El material de soporte no es necesario pues la pieza se diseñó para ser impresa sin este, pero se recomienda su uso para que no se comprometa la calidad e integridad de las piezas.

39

## Fase de Impresión

No. Parte: | Nombre: Art3TensionerPulley | Cliente: LIANA | Material: PLA MAX
Op: 1 Maquina: Impresora 3D Soporte y montaje: N/A | Descripción: Imprimir la pieza y al final retirar el material de soporte u material extra como los hilos que se generan al imprimir. | | Croquis:

## Hoja de proceso

No. Plano: 36 | Nombre: Art3TensionerPulley
Gcode: N/A | Maquina: Impresora 3D
Material: PLA MAX
Instrucciones de montaje:
Imprimir la pieza en el centro del área de trabajo.
Op: | Parámetros: | Herramientas | Observaciones:
1 | Resolución de capa: 0,2mm Densidad de relleno: 40% Patrón de relleno: Giroide Imprimir con soportes: Si Temperatura del extrusor: Recomendada para el material | Impresora 3D | El material de soporte no es necesario pues la pieza se diseñó para ser impresa sin este, pero se recomienda su uso para que no se comprometa la calidad e integridad de las piezas.

40

## Fase de Impresión

No. Parte: | Nombre: CommonBearingFix | Cliente: LIANA | Material: PLA MAX
Op: 1 Maquina: Impresora 3D Soporte y montaje: N/A | Descripción: Imprimir la pieza y al final retirar el material de soporte u material extra como los hilos que se generan al imprimir. | | Croquis:

## Hoja de proceso

No. Plano: 69 | Nombre: Art2BodyA_Splitted_A
Gcode: N/A | Maquina: Impresora 3D
Material: PLA MAX
Instrucciones de montaje:
Imprimir la pieza en el centro del área de trabajo.
Op: | Parámetros: | Herramientas | Observaciones:
1 | Resolución de capa: 0,2mm Densidad de relleno: 40% Patrón de relleno: Giroide Imprimir con soportes: Si Temperatura del extrusor: Recomendada para el material | Impresora 3D

41

## Articulación 1

Todas las piezas que componen la articulación 1 se indican a continuación, como todas las piezas comparten los mismos parámetros se pueden ubicar varias piezas para impresas en el mismo ciclo de trabajo de la impresora, solo que estas se deben de juntar lo más que se pueda para reducir el tiempo de impresión, en caso de necesitar solo una pieza usar la información a continuación.

Lista de las piezas que componen la articulación:

- Art1Body
- Art2BodyACover1
- Art2MotorGear
- Art23Optodisk (ya se indicó en articulación 34)
- AxisFix (ya se indicó en articulación 34)

42

## Fase de Impresión

No. Parte: | Nombre: | Cliente: | Material:
| Art1Body | LIANA | PLA MAX
Op:
1 | Descripción: | | Croquis:

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

Maquina:
Impresora 3D

Soporte y
montaje:
N/A

## Hoja de proceso

No. Plano: 18 | Nombre: | Art1Body
Gcode: N/A | Maquina: Impresora 3D
Material: PLA MAX
Instrucciones de montaje:
Imprimir la pieza en el centro del área de trabajo.
Op: | Parámetros: | Herramientas | Observaciones:
1 | Resolución de capa: 0,2mm Densidad de relleno: 40% Patrón de relleno: Giroide Imprimir con soportes: Si Temperatura del extrusor: Recomendada para el material | Impresora 3D | El material de soporte no es necesario pues la pieza se diseñó para ser impresa sin este, pero se recomienda su uso para que no se comprometa la calidad e integridad de las piezas.

43

## Fase de Impresión

No. Parte: | Nombre: Art2BodyACover1 | Cliente: LIANA | Material: PLA MAX
Op: 1 Maquina: Impresora 3D Soporte y montaje: N/A | Descripción: Imprimir la pieza y al final retirar el material de soporte u material extra como los hilos que se generan al imprimir. | | Croquis:

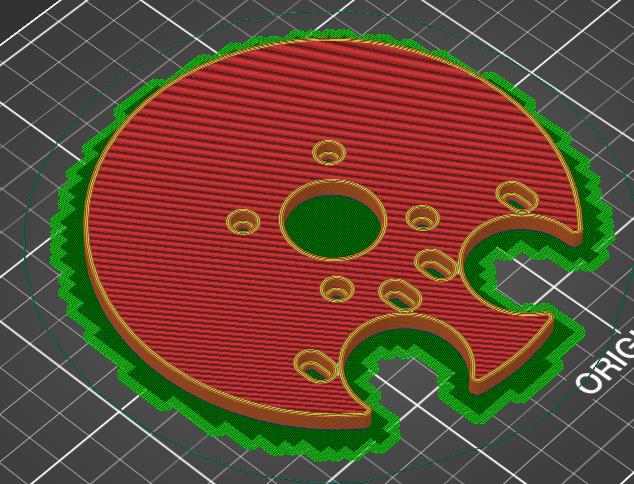
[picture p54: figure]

## Hoja de proceso

No. Plano: 26 | Nombre: Art2BodyACover1
Gcode: N/A | Maquina: Impresora 3D
Material: PLA MAX
Instrucciones de montaje:
Imprimir la pieza en el centro del área de trabajo.
Op: | Parámetros: | Herramientas | Observaciones:
1 | Resolución de capa: 0,2mm Densidad de relleno: 40% Patrón de relleno: Giroide Imprimir con soportes: Si Temperatura del extrusor: Recomendada para el material | Impresora 3D

44

## Fase de Impresión

No. Parte: | Nombre: Art2MotorGear | Cliente: LIANA | Material: PLA MAX
Op: 1 Maquina: Impresora 3D Soporte y montaje: N/A | Descripción: Imprimir la pieza y al final retirar el material de soporte u material extra como los hilos que se generan al imprimir. | | Croquis:

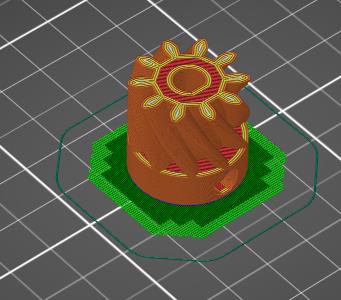
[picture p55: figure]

## Hoja de proceso

No. Plano: 34 | Nombre: Art2MotorGear
Gcode: N/A | Maquina: Impresora 3D
Material: PLA MAX
Instrucciones de montaje:
Imprimir la pieza en el centro del área de trabajo.
Op: | Parámetros: | Herramientas | Observaciones:
1 | Resolución de capa: 0,2mm Densidad de relleno: 40% Patrón de relleno: Giroide Imprimir con soportes: Si Temperatura del extrusor: Recomendada para el material | Impresora 3D

45

## Base y case del PCB

Todas las piezas que componen la articulación 1 se indican a continuación, como todas las piezas comparten los mismos parámetros se pueden ubicar varias piezas para impresas en el mismo ciclo de trabajo de la impresora, solo que estas se deben de juntar lo más que se pueda para reducir el tiempo de impresión, en caso de necesitar solo una pieza usar la información a continuación.

Lista de las piezas que componen la articulación:

- Art1Bot
- Art1GearMotor
- Art1GearPot
- Art1PotMount
- Art1Top
- BaseBearingFix
- BaseBot
- BaseCase_splitA
- BaseCase_splitB
- BaseTop
- CaseTop_splitA
- CaseTop_splitB

46

## Fase de Impresión

No. Parte: | Nombre: Art1Bot | Cliente: LIANA | Material: PLA MAX
Op: 1 Maquina: Impresora 3D Soporte y montaje: N/A | Descripción: Imprimir la pieza y al final retirar el material de soporte u material extra como los hilos que se generan al imprimir. | | Croquis:

## Hoja de proceso

No. Plano: 19 | Nombre: | Art1Bot
Gcode: N/A | Maquina: Impresora 3D
Material: PLA MAX
Instrucciones de montaje:
Imprimir la pieza en el centro del área de trabajo.
Op: | Parámetros: | Herramientas | Observaciones:
1 | Resolución de capa: 0,2mm Densidad de relleno: 40% Patrón de relleno: Giroide Imprimir con soportes: Si Temperatura del extrusor: Recomendada para el material | Impresora 3D | El material de soporte no es necesario pues la pieza se diseñó para ser impresa sin este, pero se recomienda su uso para que no se comprometa la calidad e integridad de las piezas.

47

## Fase de Impresión

No. Parte: | Nombre: Art1GearMotor | Cliente: LIANA | Material: PLA MAX
Op: 1 Maquina: Impresora 3D Soporte y montaje: N/A | Descripción: Imprimir la pieza y al final retirar el material de soporte u material extra como los hilos que se generan al imprimir. | | Croquis:

## Hoja de proceso

No. Plano: 20 | Nombre: Art1GearMotor
Gcode: N/A | Maquina: Impresora 3D
Material: PLA MAX
Instrucciones de montaje:
Imprimir la pieza en el centro del área de trabajo.
Op: | Parámetros: | Herramientas | Observaciones:
1 | Resolución de capa: 0,2mm Densidad de relleno: 40% Patrón de relleno: Giroide Imprimir con soportes: Si Temperatura del extrusor: Recomendada para el material | Impresora 3D

48

## Fase de Impresión

No. Parte: | Nombre: Art1GearPot | Cliente: LIANA | Material: PLA MAX
Op: 1 Maquina: Impresora 3D Soporte y montaje: N/A | Descripción: Imprimir la pieza y al final retirar el material de soporte u material extra como los hilos que se generan al imprimir. | | Croquis:

## Hoja de proceso

No. Plano: 21 | Nombre: | Art1GearPot
Gcode: N/A | Maquina: Impresora 3D
Material: PLA MAX
Instrucciones de montaje:
Imprimir la pieza en el centro del área de trabajo.
Op: | Parámetros: | Herramientas | Observaciones:
1 | Resolución de capa: 0,2mm Densidad de relleno: 40% Patrón de relleno: Giroide Imprimir con soportes: Si Temperatura del extrusor: Recomendada para el material | Impresora 3D

49

## Fase de Impresión

No. Parte: | Nombre: Art1PotMount | Cliente: LIANA | Material: PLA MAX
Op: 1 Maquina: Impresora 3D Soporte y montaje: N/A | Descripción: Imprimir la pieza y al final retirar el material de soporte u material extra como los hilos que se generan al imprimir. | | Croquis:

## Hoja de proceso

No. Plano: 22 | Nombre: Art1PotMount
Gcode: N/A | Maquina: Impresora 3D
Material: PLA MAX
Instrucciones de montaje:
Imprimir la pieza en el centro del área de trabajo.
Op: | Parámetros: | Herramientas | Observaciones:
1 | Resolución de capa: 0,2mm Densidad de relleno: 40% Patrón de relleno: Giroide Imprimir con soportes: Si Temperatura del extrusor: Recomendada para el material | Impresora 3D | El material de soporte no es necesario pues la pieza se diseñó para ser impresa sin este, pero se recomienda su uso para que no se comprometa la calidad e integridad de las piezas.

50

## Fase de Impresión

No. Parte: | Nombre: Art1Top | Cliente: LIANA | Material: PLA MAX
Op: 1 Maquina: Impresora 3D Soporte y montaje: N/A | Descripción: Imprimir la pieza y al final retirar el material de soporte u material extra como los hilos que se generan al imprimir. | | Croquis:

## Hoja de proceso

No. Plano: 23 | Nombre: | Art1Top
Gcode: N/A | Maquina: Impresora 3D
Material: PLA MAX
Instrucciones de montaje:
Imprimir la pieza en el centro del área de trabajo.
Op: | Parámetros: | Herramientas | Observaciones:
1 | Resolución de capa: 0,2mm Densidad de relleno: 40% Patrón de relleno: Giroide Imprimir con soportes: Si Temperatura del extrusor: Recomendada para el material | Impresora 3D | El material de soporte no es necesario pues la pieza se diseñó para ser impresa sin este, pero se recomienda su uso para que no se comprometa la calidad e integridad de las piezas.

51

## Fase de Impresión

No. Parte: | Nombre: BaseBearingFix | Cliente: LIANA | Material: PLA MAX
Op: 1 Maquina: Impresora 3D Soporte y montaje: N/A | Descripción: Imprimir la pieza y al final retirar el material de soporte u material extra como los hilos que se generan al imprimir. | | Croquis:

## Hoja de proceso

No. Plano: 57 | Nombre: BaseBearingFix
Gcode: N/A | Maquina: Impresora 3D
Material: PLA MAX
Instrucciones de montaje:
Imprimir la pieza en el centro del área de trabajo.
Op: | Parámetros: | Herramientas | Observaciones:
1 | Resolución de capa: 0,2mm Densidad de relleno: 40% Patrón de relleno: Giroide Imprimir con soportes: Si Temperatura del extrusor: Recomendada para el material | Impresora 3D

52

## Fase de Impresión

No. Parte: | Nombre: BaseBot | Cliente: LIANA | Material: PLA MAX
Op: 1 Maquina: Impresora 3D Soporte y montaje: N/A | Descripción: Imprimir la pieza y al final retirar el material de soporte u material extra como los hilos que se generan al imprimir. | | Croquis:


## Hoja de proceso

No. Plano: 58 | Nombre: | BaseBot
Gcode: N/A | Maquina: Impresora 3D
Material: PLA MAX
Instrucciones de montaje:
Imprimir la pieza en el centro del área de trabajo.
Op: | Parámetros: | Herramientas | Observaciones:
1 | Resolución de capa: 0,2mm Densidad de relleno: 40% Patrón de relleno: Giroide Imprimir con soportes: Si Temperatura del extrusor: Recomendada para el material | Impresora 3D | El material de soporte no es necesario pues la pieza se diseñó para ser impresa sin este, pero se recomienda su uso para que no se comprometa la calidad e integridad de las piezas.

53

## Fase de Impresión

No. Parte: | Nombre: BaseCase_splitA | Cliente: LIANA | Material: PLA MAX
Op: 1 Maquina: Impresora 3D Soporte y montaje: N/A | Descripción: Imprimir la pieza y al final retirar el material de soporte u material extra como los hilos que se generan al imprimir. | | Croquis:

## Hoja de proceso

No. Plano: 59 | Nombre: BaseCase_splitA
Gcode: N/A | Maquina: Impresora 3D
Material: PLA MAX
Instrucciones de montaje:
Imprimir la pieza en el centro del área de trabajo.
Op: | Parámetros: | Herramientas | Observaciones:
1 | Resolución de capa: 0,2mm Densidad de relleno: 40% Patrón de relleno: Giroide Imprimir con soportes: Si Temperatura del extrusor: Recomendada para el material | Impresora 3D | El material de soporte no es necesario pues la pieza se diseñó para ser impresa sin este, pero se recomienda su uso para que no se comprometa la calidad e integridad de las piezas.

54

## Fase de Impresión

No. Parte: | Nombre: BaseCase_splitB | Cliente: LIANA | Material: PLA MAX
Op: 1 Maquina: Impresora 3D Soporte y montaje: N/A | Descripción: Imprimir la pieza y al final retirar el material de soporte u material extra como los hilos que se generan al imprimir. | | Croquis:

## Hoja de proceso

No. Plano: 59 | Nombre: BaseCase_splitB
Gcode: N/A | Maquina: Impresora 3D
Material: PLA MAX
Instrucciones de montaje:
Imprimir la pieza en el centro del área de trabajo.
Op: | Parámetros: | Herramientas | Observaciones:
1 | Resolución de capa: 0,2mm Densidad de relleno: 40% Patrón de relleno: Giroide Imprimir con soportes: Si Temperatura del extrusor: Recomendada para el material | Impresora 3D | El material de soporte no es necesario pues la pieza se diseñó para ser impresa sin este, pero se recomienda su uso para que no se comprometa la calidad e integridad de las piezas.

55

## Fase de Impresión

No. Parte: | Nombre: BaseTop | Cliente: LIANA | Material: PLA MAX
Op: 1 Maquina: Impresora 3D Soporte y montaje: N/A | Descripción: Imprimir la pieza y al final retirar el material de soporte u material extra como los hilos que se generan al imprimir. | | Croquis:


## Hoja de proceso

No. Plano: 60 | Nombre: | BaseTop
Gcode: N/A | Maquina: Impresora 3D
Material: PLA MAX
Instrucciones de montaje:
Imprimir la pieza en el centro del área de trabajo.
Op: | Parámetros: | Herramientas | Observaciones:
1 | Resolución de capa: 0,2mm Densidad de relleno: 40% Patrón de relleno: Giroide Imprimir con soportes: Si Temperatura del extrusor: Recomendada para el material | Impresora 3D | El material de soporte no es necesario pues la pieza se diseñó para ser impresa sin este, pero se recomienda su uso para que no se comprometa la calidad e integridad de las piezas.

56

## Fase de Impresión

No. Parte: | Nombre: CaseTop_splitA | Cliente: LIANA | Material: PLA MAX
Op: 1 Maquina: Impresora 3D Soporte y montaje: N/A | Descripción: Imprimir la pieza y al final retirar el material de soporte u material extra como los hilos que se generan al imprimir. | | Croquis:


## Hoja de proceso

No. Plano: 61 | Nombre: CaseTop_splitA
Gcode: N/A | Maquina: Impresora 3D
Material: PLA MAX
Instrucciones de montaje:
Imprimir la pieza en el centro del área de trabajo.
Op: | Parámetros: | Herramientas | Observaciones:
1 | Resolución de capa: 0,2mm Densidad de relleno: 20% Patrón de relleno: Giroide Imprimir con soportes: Si Temperatura del extrusor: Recomendada para el material | Impresora 3D | Al ser tapas no es necesario que este a todo relleno, de hecho, si el relleno es elevado se puede pandear o doblar.

57

## Fase de Impresión

No. Parte: | Nombre: CaseTop_splitB | Cliente: LIANA | Material: PLA MAX
Op: 1 Maquina: Impresora 3D Soporte y montaje: N/A | Descripción: Imprimir la pieza y al final retirar el material de soporte u material extra como los hilos que se generan al imprimir. | | Croquis:


## Hoja de proceso

No. Plano: 61 | Nombre: CaseTop_splitB
Gcode: N/A | Maquina: Impresora 3D
Material: PLA MAX
Instrucciones de montaje:
Imprimir la pieza en el centro del área de trabajo.
Op: | Parámetros: | Herramientas | Observaciones:
1 | Resolución de capa: 0,2mm Densidad de relleno: 20% Patrón de relleno: Giroide Imprimir con soportes: Si Temperatura del extrusor: Recomendada para el material | Impresora 3D | Al ser tapas no es necesario que este a todo relleno, de hecho, si el relleno es elevado se puede pandear o doblar.

58

## Gripper

Todas las piezas que componen el gripper o efector se indican a continuación, como todas las piezas comparten los mismos parámetros se pueden ubicar varias piezas para impresas en el mismo ciclo de trabajo de la impresora, solo que estas se deben de juntar lo más que se pueda para reducir el tiempo de impresión, en caso de necesitar solo una pieza usar la información a continuación.

Lista de las piezas que componen la articulación:

- GripperActiveArm
- GripperArm
- GripperBot
- GripperFinger
- GripperPassiveArm
- GripperTop

59

## Fase de Impresión

No. Parte: | Nombre: GripperActiveArm | Cliente: LIANA | Material: PLA MAX
Op: 1 Maquina: Impresora 3D Soporte y montaje: N/A | Descripción: Imprimir la pieza y al final retirar el material de soporte u material extra como los hilos que se generan al imprimir. | | Croquis:


## Hoja de proceso

No. Plano: 62 | Nombre: GripperActiveArm
Gcode: N/A | Maquina: Impresora 3D
Material: PLA MAX
Instrucciones de montaje:
Imprimir la pieza en el centro del área de trabajo.
Op: | Parámetros: | Herramientas | Observaciones:
1 | Resolución de capa: 0,2mm Densidad de relleno: 40% Patrón de relleno: Giroide Imprimir con soportes: Si Temperatura del extrusor: Recomendada para el material | Impresora 3D

60

## Fase de Impresión

No. Parte: | Nombre: GripperArm | Cliente: LIANA | Material: PLA MAX
Op: 1 Maquina: Impresora 3D Soporte y montaje: N/A | Descripción: Imprimir la pieza y al final retirar el material de soporte u material extra como los hilos que se generan al imprimir. | | Croquis:

## Hoja de proceso

No. Plano: 63 | Nombre: | GripperArm
Gcode: N/A | Maquina: Impresora 3D
Material: PLA MAX
Instrucciones de montaje:
Imprimir la pieza en el centro del área de trabajo.
Op: | Parámetros: | Herramientas | Observaciones:
1 | Resolución de capa: 0,2mm Densidad de relleno: 40% Patrón de relleno: Giroide Imprimir con soportes: Si Temperatura del extrusor: Recomendada para el material | Impresora 3D

61

## Fase de Impresión

No. Parte: | Nombre: GripperBot | Cliente: LIANA | Material: PLA MAX
Op: 1 Maquina: Impresora 3D Soporte y montaje: N/A | Descripción: Imprimir la pieza y al final retirar el material de soporte u material extra como los hilos que se generan al imprimir. | | Croquis:


## Hoja de proceso

No. Plano: 64 | Nombre: | GripperBot
Gcode: N/A | Maquina: Impresora 3D
Material: PLA MAX
Instrucciones de montaje:
Imprimir la pieza en el centro del área de trabajo.
Op: | Parámetros: | Herramientas | Observaciones:
1 | Resolución de capa: 0,2mm Densidad de relleno: 40% Patrón de relleno: Giroide Imprimir con soportes: Si Temperatura del extrusor: Recomendada para el material | Impresora 3D | El material de soporte no es necesario pues la pieza se diseñó para ser impresa sin este, pero se recomienda su uso para que no se comprometa la calidad e integridad de las piezas.

62

## Fase de Impresión

No. Parte: | Nombre: GripperFinger | Cliente: LIANA | Material: PLA MAX
Op: 1 Maquina: Impresora 3D Soporte y montaje: N/A | Descripción: Imprimir la pieza y al final retirar el material de soporte u material extra como los hilos que se generan al imprimir. | | Croquis:


## Hoja de proceso

No. Plano: 65 | Nombre: GripperFinger
Gcode: N/A | Maquina: Impresora 3D
Material: PLA MAX
Instrucciones de montaje:
Imprimir la pieza en el centro del área de trabajo.
Op: | Parámetros: | Herramientas | Observaciones:
1 | Resolución de capa: 0,2mm Densidad de relleno: 40% Patrón de relleno: Giroide Imprimir con soportes: Si Temperatura del extrusor: Recomendada para el material | Impresora 3D | El material de soporte no es necesario pues la pieza se diseñó para ser impresa sin este, pero se recomienda su uso para que no se comprometa la calidad e integridad de las piezas.

63

## Fase de Impresión

No. Parte: | Nombre: GripperPassiveArm | Cliente: LIANA | Material: PLA MAX
Op: 1 Maquina: Impresora 3D Soporte y montaje: N/A | Descripción: Imprimir la pieza y al final retirar el material de soporte u material extra como los hilos que se generan al imprimir. | | Croquis:

## Hoja de proceso

No. Plano: 66 | Nombre: GripperPassiveArm
Gcode: N/A | Maquina: Impresora 3D
Material: PLA MAX
Instrucciones de montaje:
Imprimir la pieza en el centro del área de trabajo.
Op: | Parámetros: | Herramientas | Observaciones:
1 | Resolución de capa: 0,2mm Densidad de relleno: 40% Patrón de relleno: Giroide Imprimir con soportes: Si Temperatura del extrusor: Recomendada para el material | Impresora 3D

64

## Fase de Impresión

No. Parte: | Nombre: GripperTop | Cliente: LIANA | Material: PLA MAX
Op: 1 Maquina: Impresora 3D Soporte y montaje: N/A | Descripción: Imprimir la pieza y al final retirar el material de soporte u material extra como los hilos que se generan al imprimir. | | Croquis:


## Hoja de proceso

No. Plano: 67 | Nombre: | GripperTop
Gcode: N/A | Maquina: Impresora 3D
Material: PLA MAX
Instrucciones de montaje:
Imprimir la pieza en el centro del área de trabajo.
Op: | Parámetros: | Herramientas | Observaciones:
1 | Resolución de capa: 0,2mm Densidad de relleno: 40% Patrón de relleno: Giroide Imprimir con soportes: Si Temperatura del extrusor: Recomendada para el material | Impresora 3D | El material de soporte no es necesario pues la pieza se diseñó para ser impresa sin este, pero se recomienda su uso para que no se comprometa la calidad e integridad de las piezas.

65

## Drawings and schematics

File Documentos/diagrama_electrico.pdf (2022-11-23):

# GND ⁺¹²V

# GND ⁺¹²V

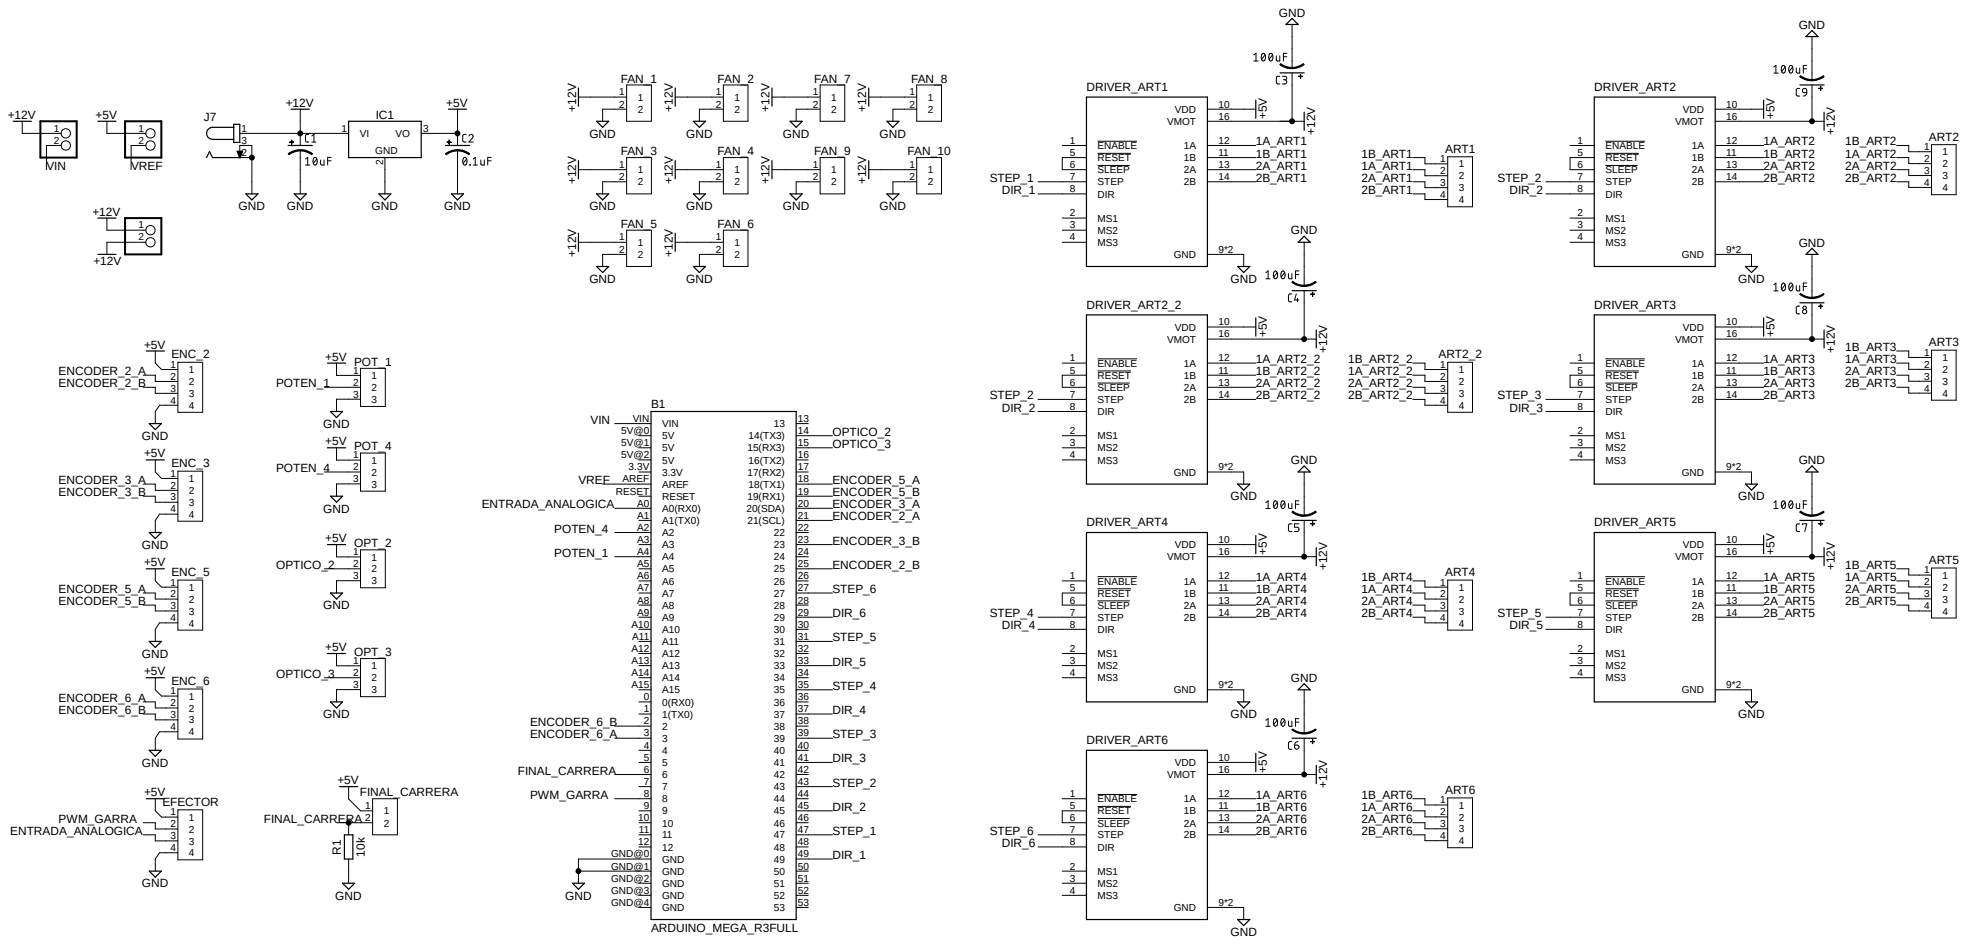
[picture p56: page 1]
ARDUINO_MEGA_R3FULL; GND; +12V +12V ⁺¹²V; +12V ⁺¹²V ⁺¹²V; GND ⁺¹²V; GND +12V; RESET RESET; GND GND@4; GND GND@0; GND GND@1; GND GND@2; GND GND@3; 5V 5V@2 3.3V 3.3V AREF AREF; 21(SCL); 21 20(SDA); 19 VIN VIN; DRIVER_ART1 ENABLE 1; 12 RESET 5; SLEEP 6; STEP 7; DIR 8; 14 VDD; 10 VMOT; 16 GND; DRIVER_ART2 ENABLE 1; 10 VMOT 16 GND; 9*2 DRIVER_ART3 ENABLE 1; 9*2 DRIVER_ART4 ENABLE 1; DRIVER_ART5 ENABLE 1; 9*2 DRIVER_ART6 ENABLE 1; DRIVER_ART2_2 ENABLE 1; IC1 GND; 3 ART1; 4 ART3; ART2 1; ART4 1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

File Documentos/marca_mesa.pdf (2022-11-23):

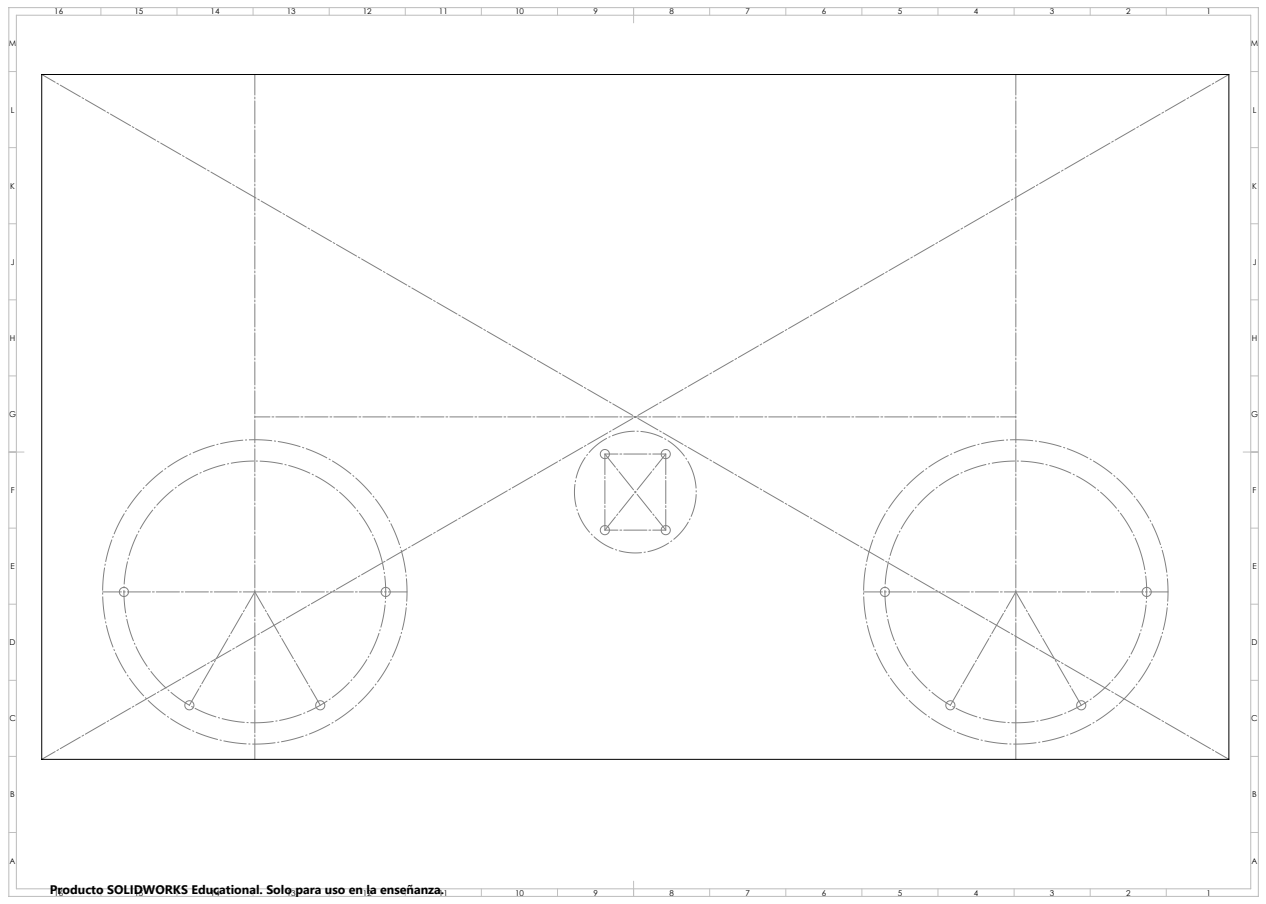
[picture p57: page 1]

Producto SOLIDWORKS Educational. Solo para uso en la enseñanza.

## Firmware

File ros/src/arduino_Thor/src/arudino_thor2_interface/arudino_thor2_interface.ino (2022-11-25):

//librerias necesarias para el funcionamiento
#include <Servo.h>
#include <Encoder.h>
#include <AccelStepper.h>
#include <MultiStepper.h>

//mensajes y componenetes necesarios de ros
#include <ros.h>
#include <control_msgs/GripperCommand.h>
#include <arduino_Thor/joints_steps.h>
#include <arduino_Thor/sensors_raw.h>
#include <std_msgs/Int16.h>
#include <std_msgs/UInt16.h>
#include <std_msgs/Bool.h>
#include <std_msgs/String.h>


// Aca se nombran a todos los motores de las articulaciones, si bien hay 7 motores 
// ya que en la articuaclion se conenctan dos drivers 
AccelStepper Art1(AccelStepper::DRIVER, 47, 49); //step dir
AccelStepper Art2(AccelStepper::DRIVER, 43, 45); //step dir
AccelStepper Art3(AccelStepper::DRIVER, 39, 41); //step dir
AccelStepper Art4(AccelStepper::DRIVER, 35, 37); //step dir
AccelStepper Art5(AccelStepper::DRIVER, 31, 33); //step dir
AccelStepper Art6(AccelStepper::DRIVER, 27, 29); //step dir


// Se pueden colcoar hasta 10 steppers en el grupo MultiStepper
MultiStepper motores;

// se crea el servo del efector final y la señal extra afuturo 
Servo efector;
#define analextra A0

// se definen los finales de carrera y a cuales pinesestan conectados 
#define limite56 6
#define limite3 15
#define limite2 14

// se indica el nombre de los potenciometros y se asigan a los pines analogicos 
#define pot4 A2
#define pot1 A4
int lecp4;
int lecp1;

// se crean los encoders del thor
Encoder Enc6(3, 2);
Encoder Enc5(18, 19);
Encoder Enc3(20, 23);
Encoder Enc2(21, 25);




// se crea el node handle
ros::NodeHandle  nh;

// se indica el mensaje a publicar y el tipo de mensaje al nodo
arduino_Thor::sensors_raw sensors;
ros::Publisher sensorData("sensor_raw_Thor2", &sensors );
 

//funcion que llama el nodo cuando recibe informacion de control de gripper
void servocmd( const control_msgs::GripperCommand& msg){

  efector.write(msg.position); 

}


//funcion que llama el nodo cuando recibe informacion de control de articulaciones
void arts( const arduino_Thor::joints_steps& joints){
  
  long pos[6]; // conjunto de posiciones que se desean alcanzar
   
  pos[0] = joints.joint_1;   //pulsos de art1
  pos[1] = joints.joint_2;    //pulsos de art2
  pos[2] = joints.joint_3;  //pulsos de art3
  pos[3] = joints.joint_4;   //pulsos de art4 
  
  pos[4] = joints.joint_5;    //pulsos de art5 movimiento traslacion 
  pos[5] = joints.joint_6;  //pulsos de art6 movimiento traslacion 
    
  motores.moveTo(pos);
  motores.runSpeedToPosition(); 


  sensors.joint_1= analogRead(pot1);
  sensors.joint_2= Enc2.read();
  sensors.joint_3= Enc3.read();
  sensors.joint_4= analogRead(pot4);
  sensors.joint_5= Enc5.read();
  sensors.joint_6= Enc6.read();

 
  sensorData.publish(&sensors );
  delay(5);

  pos[4] = joints.joint_5post;    //pulsos de art5 movimiento rotacion
  pos[5] = joints.joint_6post;  //pulsos de art6 movimiento rotacion

  motores.moveTo(pos);
  motores.runSpeedToPosition(); 
  
  sensors.joint_5= Enc5.read();
  sensors.joint_6= Enc6.read();
  
  sensorData.publish(&sensors );

}



// se indican los subcriptores del nodo, reciben la informacion para controlar el thor

ros::Subscriber<control_msgs::GripperCommand> sub("gripper_Thor2", &servocmd);
ros::Subscriber<arduino_Thor::joints_steps> arduino_joints("joints_steps_thor2", &arts);


void setup() {
  // put your setup code here, to run once:

  efector.attach(8);// se in dica a cual pin se conecta el servo
  // se indican los pines de finales de carrera como entradas 
  pinMode(limite56, INPUT);
  pinMode(limite3, INPUT);
  pinMode(limite2, INPUT);
  
  nh.initNode();
  nh.subscribe(sub);
  nh.subscribe(arduino_joints);
  nh.advertise(sensorData);

  // Se añañaden los steppers al grupo de MultiStepper para que sea controlados
  motores.addStepper(Art1);
  motores.addStepper(Art2);
  motores.addStepper(Art3);
  motores.addStepper(Art4);
  motores.addStepper(Art5);
  motores.addStepper(Art6);

  //se ejecuta el home del thor
  Thor_Home();
  sensorData.publish(&sensors );
}

void loop() {
  // put your main code here, to run repeatedly:

  nh.spinOnce();
  delay(1);

}




void Thor_Home(){

  // Se configura la velocidad maxima de cada motor 
  Art1.setMaxSpeed(100);
  Art2.setMaxSpeed(100);
  Art3.setMaxSpeed(100);
  Art4.setMaxSpeed(100);
  Art5.setMaxSpeed(100);
  Art6.setMaxSpeed(100);


//====================================================
//========== Se ajusta la articulacion 2 =============
//====================================================
  int home2=-1; //variable para hacer home
  
 //Articulacion 2 se mueve hasta que el final de carrera optico se ponga en low
  while(digitalRead(limite2)){
    Art2.moveTo(home2);
    Art2.run();
    home2--;
    delay(1);
    }
    
  //Se pone la posicion actual del motor
  Art2.setCurrentPosition(0);
  // Se asignan los parametros del motor
  Art2.setMaxSpeed(100);
  Art2.setAcceleration(100);
  //se coloca el encoder en 0
  Enc2.write(0);

//====================================================
//========== Se ajusta la articulacion 3 =============
//====================================================
  int home3=1; //variable para hacer home
  
 //Articulacion 3 se mueve hasta que el final de carrera optico se ponga en low
  while(digitalRead(limite3)){
    Art3.moveTo(home3);
    Art3.run();
    home3++;
    delay(1);
    }
    
  //Se pone la posicion actual del motor
  Art3.setCurrentPosition(0);
  // Se asignan los parametros del motor
  Art3.setMaxSpeed(100);
  Art3.setAcceleration(100);
  //se coloca el encoder en 0
  Enc3.write(0);

//====================================================
//========== Se ajusta la articulacion 1 =============
//====================================================

//Para el brazo numero 1 el inicio o cero se encuntra en 
//Para el brazo numero 2 el inicio o cero se encuntra en 497
//por lo que se debe hacer el home a esa posicion respectiva

  int home1=0; //variable para hacer home
  while(analogRead(pot1)!=518){
    if(analogRead(pot1) > 518){
      home1--;
      Art1.moveTo(home1);
      Art1.run();
      delay(1); 
      }
     else{
      home1++;
      Art1.moveTo(home1);
      Art1.run();
      delay(1); 
     }
    }
  //Se pone la posicion actual del motor
  Art1.setCurrentPosition(0);
  // Se asignan los parametros del motor
  Art1.setMaxSpeed(100);
  Art1.setAcceleration(100);

  
//====================================================
//========== Se ajusta la articulacion 1 =============
//====================================================
//Para el brazo numero 1 el inicio o cero se encuntra en 
//Para el brazo numero 2 el inicio o cero se encuntra en 651
//por lo que se debe hacer el home a esa posicion respectiva

  int home4=0; //variable para hacer home
  while(analogRead(pot4)!=680){
    if(analogRead(pot4) > 680){
      home4++;
      Art4.moveTo(home4);
      Art4.run();
      delay(1); 
      }
     else{
      home4--;
      Art4.moveTo(home4);
      Art4.run();
      delay(1); 
     }
    }
  //Se pone la posicion actual del motor
  Art4.setCurrentPosition(0);
  // Se asignan los parametros del motor
  Art4.setMaxSpeed(100);
  Art4.setAcceleration(100);

  
//====================================================
//========= Se ajusta el sistema diferencial =========
//====================================================

  int home56=-1; //variable para hacer home
  long positions[6];
    
 //Articulacion 56 se mueve hasta que toque el final de carrera
  while(digitalRead(limite56)){
    Art5.moveTo(-home56);
    Art6.moveTo(home56);
    Art5.run();
    Art6.run();
    home56--;
    delay(1);
    }
 home56=1;
 //Articulacion 56 se devuelve hasta que deje de activar el final de carrera
  while(!digitalRead(limite56)){
    Art5.moveTo(-home56);
    Art6.moveTo(home56);
    Art5.run();
    Art6.run();
    home56++;
    delay(1);
    }

  //Se pone la posicion actual del motor
  Art5.setCurrentPosition(-127);
  Art6.setCurrentPosition(127);
  
  // Se asignan los parametros de los motores
  Art5.setMaxSpeed(100);
  Art6.setMaxSpeed(100);
  Art5.setAcceleration(100);
  Art6.setAcceleration(100);
  
  // se colocan los encoders a 90 grados
  Enc5.write(500);
  Enc6.write(-500); 

// se mueve los motores para que ponga en 0 el sistema diferencial
  positions[0] = 0;   //pulsos de art1
  positions[1] = 0;    //pulsos de art2
  positions[2] = 0;  //pulsos de art3
  positions[3] = 0;   //pulsos de art4
  positions[4] = 0;    //pulsos de art5
  positions[5] = 0;  //pulsos de art6
  motores.moveTo(positions);
  motores.runSpeedToPosition();

}
